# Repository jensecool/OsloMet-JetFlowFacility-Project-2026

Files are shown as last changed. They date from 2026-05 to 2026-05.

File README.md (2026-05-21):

# OsloMet Jet Flow Facility Project 2026

Technical information, firmware, 3D models, and documentation for the extended sub-sonic jet flow facility in the OsloMet Green Energy Lab. This repository continues the work of the 2025 group and adds quantitative airflow measurement to the facility.

## Project Background

This project is part of the European Project Semester (EPS) 2026 at Oslo Metropolitan University. Group 5 has extended an existing single-jet flow facility (originally built by Group 2 in 2025) with a differential pressure sensor and real-time velocity computation, turning a previously qualitative demonstration into a quantitative student experiment.

## Features

- **Fan Control:**
Adjustable fan speed via potentiometer and PWM output, with real-time RPM monitoring using a tachometer input.
- **Speaker Control:**
Potential for speaker volume adjustment via a second potentiometer.
- **Pressure and Velocity Measurement (new):**
Differential pressure across the stagnation chamber is read over I2C and converted to air velocity using Bernoulli's equation.
- **LCD Display:**
A Grove RGB LCD shows the fan speed, the live differential pressure (Pa), and the computed velocity (m/s). See the note below on the single versus dual screen configuration.
- **I2C Multiplexer:**
A TCA9548A multiplexer manages multiple I2C devices (the LCD(s) and the pressure sensor) on a single ESP32 I2C bus.
- **Switch Control:**
A momentary power switch toggles the fan system on and off using edge detection in firmware.
- **Multicore Task Management:**
Fan and switch handling tasks are pinned to separate ESP32 cores for parallel processing.

## Important Note: Single Screen vs Two Screens

The original design used two Grove RGB LCD screens: one for fan speed and one for pressure and velocity. During development the onboard 3.3V voltage regulator of the ESP32 was damaged, most likely during an earlier incident where the I2C hub was destroyed by a loose ground connection under power.

A healthy ESP32 regulator should output 3.3V. After the damage, the regulator only produces about 2.7V even with a healthy 5V input on VIN. This lower voltage is enough to power one LCD with readable contrast, but two LCD backlights together draw too much current, which pulls the voltage down further and makes the text on both screens too faint to read.

Because of this, the current working setup uses a single LCD that shows all values on one screen. When the ESP32 is replaced with a board that has a working 3.3V regulator, the two screen version can be used again.

Two firmware versions are provided:

- `esp-code/esp-code.ino` is the single screen version. All values (fan speed, velocity, and pressure) are shown on one LCD connected to hub channel 0. This is the version that works with the current damaged ESP32.
- `esp-code/esp_code-2screens/` contains the two screen version. Fan speed is shown on the LCD on hub channel 0, and pressure and velocity are shown on the LCD on hub channel 1. Use this version only with an ESP32 that has a healthy 3.3V regulator.

## Installation Instructions

### Hardware Requirements

- ESP32 NodeMCU-32S Development Board
- Fan motor with tachometer feedback (12V DC, 1.3A)
- 1x or 2x Grove RGB LCD V5.0 (I2C interface), depending on the firmware version used
- TCA9548A I2C multiplexer hub
- ELVH-M250D-HRRJ-I-N3A5 differential pressure sensor (±250 mbar, I2C address 0x38)
- Mean Well SD-15A-05 DC-DC converter (12V to 5V, 3A)
- Potentiometers (for fan speed and speaker volume)
- Switches (for power and speaker control)
- LEDs (for status indication)
- 50W audio amplifier with 5" 4Ω speaker
- Supporting resistors and wiring

### Software Requirements

- Arduino IDE (2.x or later)
- NodeMCU-32S board support (ESP32 boards package)

### Arduino Libraries

- `Wire.h`
- `Arduino.h`
- `rgb_lcd.h`

### Installation Steps

1. Clone this repository:
```bash
   git clone https://github.com/jensecool/OsloMet-JetFlowFacility-Project-2026.git
```

2. Open the firmware you need in the Arduino IDE:
   - `esp-code/esp-code.ino` for the single screen setup (current hardware)
   - `esp-code/esp_code-2screens/` for the two screen setup (requires a healthy ESP32)
3. Install the necessary libraries via the Library Manager.
4. Select the NodeMCU-32S board and the correct COM port.
5. Upload the code.

## Repository Structure

```
OsloMet-JetFlowFacility-Project-2026/
├── 3d models/         3D model files for printable enclosures and adapters
├── Circuit design/    Schematic diagrams of the electronics
├── esp-code/          ESP32 Arduino firmware (single and two screen versions)
├── Flowchart/         Flowcharts of the code logic and experiment process
└── Worksheet/         Student experiment worksheet
```

## ESP32 Pinout

| Function                | ESP32 Pin | Description                            |
|:------------------------|:----------|:---------------------------------------|
| Power Switch Input      | 5         | Toggles fan system ON/OFF              |
| Fan Speed Potentiometer | 34        | Analog read for fan speed setting      |
| Power LED Output        | 13        | Indicates fan system status            |
| Fan PWM Control         | 25        | PWM signal to control fan speed        |
| Fan Tachometer Input    | 14        | Reads pulses for RPM calculation       |
| I2C SDA                 | 21        | I2C data line to multiplexer hub       |
| I2C SCL                 | 22        | I2C clock line to multiplexer hub      |

## I2C Bus Layout

All I2C devices are connected through the TCA9548A multiplexer (address `0x70`) on the ESP32 bus:

| Hub Channel | Device                       | I2C Address     |
|:------------|:-----------------------------|:----------------|
| 0           | Main LCD (fan speed LCD)     | `0x30`, `0x3E`  |
| 1           | Pressure LCD (2 screen only) | `0x30`, `0x3E`  |
| 2           | Pressure sensor              | `0x38`          |
| 3 to 7      | Free                         | n/a             |

## Pressure Sensor Pinout

The ELVH-M250D-HRRJ-I-N3A5 sensor uses the HRRJ surface-mount J-lead package. Note that on this variant SCL is on pin 4, not pin 5 as the standard ELVH datasheet pin code table 1 suggests. The verified connections are:

| Sensor Pin | Function     | Wire Color |
|:-----------|:-------------|:-----------|
| 1          | GND          | Black      |
| 2          | Vs (3.3V)    | Red        |
| 3          | SDA          | White      |
| 4          | SCL          | Yellow     |
| 5 to 8     | Not connected| n/a        |

## Notes

- **Kickstart:** Fan starts at 100% PWM for 5 seconds on boot to overcome initial inertia.
- **I2C Multiplexer:** The project uses the TCA9548A I2C switch to manage the LCD(s) and the pressure sensor on the same I2C bus.
- **Power switch:** The APEM 5232 power switch is a momentary type. The firmware uses edge detection so that one press toggles the system on and the next press toggles it off.
- **Sensor zero offset:** The pressure sensor exhibits a small static offset (typically around 200 to 230 Pa) at zero airflow. This is normal manufacturing tolerance and should be subtracted from raw readings when computing absolute velocity values for analysis.
- **Velocity calculation:** Air velocity is computed using Bernoulli's equation `v = sqrt(2 * dP / rho)` with air density `rho = 1.225 kg/m^3`. Negative differential pressures are clamped to zero velocity in the firmware.

## Team

**Group 5, European Project Semester, OsloMet 2026:**
Jense Cool, Juan Trigueros, Alec Vroon, Siiri Vainopaa.

Supervisor: Ramis Örlü.

## Acknowledgements

This project builds upon the original jet-flow facility designed and constructed by **Group 2 (UFO – SSJFF) in 2025**: Finja Dittmann, Jelte Hoekstra, Robin Lind, Noud van der Meulen. Their report and original repository (`EPS-subsonic-jet-facility`) provided the hardware base, the smoke visualisation modules, and the acoustic forcing module that this work extends.

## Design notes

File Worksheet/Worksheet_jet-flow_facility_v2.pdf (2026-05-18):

European Project Semester, OsloMet 2026 - Group 5
Experiment: Quantitative fluid dynamics with the extended jet-flow facility

OSLO
MET
Jense Cool, Juan Trigueros, Alec Vroon, Siiri Vainopaa - Group 5 | Page 1

# Quantitative fluid dynamics with the extended jet-flow facility

## 1 Objective of the experiment

The aim of this experiment is twofold. First, students observe how a controlled stream of air behaves at different fan speeds and how an external sound source can disturb that stream. Second, and new in this version of the setup, students obtain a numerical measurement of the air velocity inside the facility by reading the differential pressure across the stagnation chamber and applying Bernoulli's equation. The facility therefore moves from a qualitative demonstration toward a small quantitative laboratory experiment.

By the end of the session the student should be able to relate a visible flow pattern to a measured pressure value, recognise the transition between laminar and turbulent regimes, and describe how acoustic forcing modifies a jet.

## 2 Theoretical fundamentals

### 2.1 Fluid dynamics

Fluid dynamics is the branch of physics that describes the motion of gases and liquids and the forces acting on them. It underpins applications as varied as aircraft design, weather prediction, blood flow modelling, and ventilation. In the laboratory it is usually approached through simplified geometries that isolate one phenomenon at a time, which is the role this facility plays.

### 2.2 The jet-flow facility

The setup used here is a single-jet wind facility. A fan draws ambient air through an intake, the airflow is conditioned by a diffuser followed by a honeycomb structure, and the resulting stream exits through a nozzle. The diffuser slows the flow so that the honeycomb can straighten it into parallel filaments, producing the laminar profile required for clean visualisation and measurement.

### 2.3 Smoke visualisation

Air on its own is invisible, so it has to be marked with a tracer to become observable. A small vaporiser produces a non-toxic glycol mist which is light enough to follow the local velocity field with very little lag. Once the mist is entrained in the airstream, the eye can clearly distinguish smooth laminar filaments from chaotic turbulent eddies.

### 2.4 Acoustic forcing

Sound consists of small periodic pressure fluctuations travelling through the air. When these fluctuations reach a jet, they perturb the shear layer at the edge of the stream and can trigger or suppress the natural instabilities that would otherwise grow further downstream. The result is a jet whose behaviour depends not only on the fan speed but also on the frequency and amplitude of the

Jense Cool, Juan Trigueros, Alec Vroon, Siiri Vainopaa - Group 5 | Page 2

imposed sound. This is referred to as acoustic forcing.

### 2.5 Pressure measurement and Bernoulli's principle

The extension added to the facility lets the user read the air velocity rather than estimate it visually. A differential pressure sensor sits between the stagnation chamber inside the facility and the ambient air outside. The difference between these two pressures, called the dynamic pressure, depends directly on the flow speed.

For an incompressible airflow at low speeds, Bernoulli's equation relates the dynamic pressure ∆P to the velocity v through:
v = √(2 · ∆P / ρ)

where ρ is the density of air, taken as 1.225 kg/m³
at standard room conditions. The microcontroller performs this calculation internally and displays both the raw pressure and the resulting velocity on the second LCD, so no manual computation is required during the session.

A few caveats are worth keeping in mind. Bernoulli's equation assumes a steady, frictionless, incompressible flow along a streamline. In a real jet these assumptions break down slightly, so the displayed velocity should be treated as a good estimate rather than an exact value. The sensor itself also has a small zero offset of roughly 200 Pa which appears as a non-zero reading even when the fan is off. Subtract this offset before drawing conclusions.

## 3 Work instructions

### 3.1 Preparing the facility

Verify before powering anything that the fan speed potentiometer (-SGA1) and the speaker volume control (-SGA2) are both turned fully counter-clockwise to the zero position. Plug the 12 V power supply (-TBA1) into a wall outlet and connect its barrel jack to the control panel inlet (-XDB1). Plug the amplifier (-TFA1) into a wall outlet using its dedicated mains cable (-XDB2). Press the power switch (-SJA1) on the control panel. The yellow LCD (-PHA1) should now show the current fan speed at 0 percent and the green LCD (-PHA2) should show a pressure reading near zero and a velocity near zero. Once both displays are active, the fan can be brought up by turning -SGA1 clockwise.

### 3.2 Reading the displays

Two LCD screens are mounted on the control panel. The yellow one shows the current fan speed as a percentage of full power, which corresponds to the position of the speed potentiometer. The green one shows two values: the differential pressure across the stagnation chamber in pascals, and the air velocity in metres per second derived from that pressure. The pressure value may oscillate by a few pascals as the sensor picks up small acoustic disturbances. This is normal and indicates that the sensor is working.

### 3.3 Smoke visualisation module

Slot the smoke machine (-HPB1) into the nozzle adapter (-NAD1) at the outlet end of the facility. Press the wireless smoke button (-SJB1) to release a puff of mist into the airflow. Vary the fan speed

Jense Cool, Juan Trigueros, Alec Vroon, Siiri Vainopaa - Group 5 | Page 3

(-SGA1) across its range and observe how the visible plume changes shape. At low speeds the smoke should travel in clean parallel layers. As the speed rises, the smoke breaks up into irregular swirling structures. Note your observations together with the corresponding pressure and velocity readings from the green LCD. Repeat the exercise with the smoke machine moved into the fan-side adapter (-NAD2) and compare the patterns at the same flow speeds.

### 3.4 Acoustic forcing module

For this part of the experiment the fan-side smoke adapter (-NAD2) should remain in place while the nozzle adapter (-NAD1) is removed. Attach the acoustic adapter (-XMB1) to the nozzle. Connect the audio cable (-XDB3) to the amplifier (-TFA1) on one end and to a phone or audio player on the other end. Toggle the speaker switch (-SJA2) to enable the speaker. Begin smoke production with (-SJB1) and play music while varying the volume with the speaker control (-SGA2). Try tracks of different genres, particularly those with strong low-frequency content, and document how the visible jet responds. Pay attention to any changes in the green LCD pressure reading during loud low-frequency passages.

### 3.5 Quantitative measurement procedure

This section is new compared to the previous version of the experiment and produces the numerical data needed for the analysis questions below.

Step 1. With the fan switched off, record the resting pressure value displayed on the green LCD. This is the sensor zero offset. Typical values fall in the range of 200 Pa to 230 Pa.
Step 2. Set the fan to 10 percent using -SGA1 and wait approximately ten seconds for the readings to stabilise. Note both the pressure and the velocity from the green LCD, together with the fan speed setting.
Step 3. Repeat at 25, 50, 75 and 100 percent fan speed. Five well spaced data points are sufficient.
Step 4. For each measurement, subtract the offset from Step 1 from the raw pressure reading. The corrected pressure is the value to use for any velocity calculation done by hand.
Step 5. Plot the corrected pressure on the vertical axis and the fan speed percentage on the horizontal axis. Then plot velocity against fan speed on a second graph. Compare the shapes of the two curves and connect them to the underlying physics in your analysis.

### 3.6 Analysis questions

Answer the following questions in your written submission. Combine visual observations from the smoke modules with numerical results from the pressure measurements where possible.

1) How does the visible behaviour of the airflow change as the fan speed increases?
2) At what approximate fan speed does the jet appear to transition from laminar to turbulent? Does this match the pressure or velocity reading at which it happens?
3) Which fluid dynamics principles explain the laminar to turbulent transition?
4) How does smoke visualisation help to interpret flow phenomena that would otherwise be invisible?

Jense Cool, Juan Trigueros, Alec Vroon, Siiri Vainopaa - Group 5 | Page 4
5) Using your recorded data, plot the measured velocity against fan speed percentage. Is the relationship linear, quadratic, or something else? Explain why this shape is expected.
6) Using your recorded data, plot the corrected pressure against fan speed percentage. How does this shape relate to the velocity curve?
7) Estimate the Reynolds number at maximum fan speed using a characteristic length equal to the nozzle diameter and a kinematic viscosity of 1.5 × 10⁻⁵ m²
/s. Does the value support your visual observation of laminar versus turbulent flow?
8) What effect does the acoustic forcing have on the visible airflow at different volumes and frequencies?
9) Through which physical mechanisms can sound waves modify the structure of a jet?
10) Discuss the main sources of measurement uncertainty in the pressure and velocity readings, and how the experiment could be improved.
11) Suggest a practical engineering application that could benefit from acoustic control of an airflow.

Jense Cool, Juan Trigueros, Alec Vroon, Siiri Vainopaa - Group 5 | Page 5

## 4 Material list

Component references follow the IEC 81346-2 standard. Items marked with an asterisk were added or modified in the current revision of the facility.

Reference | Name | Comment
-BPB1* | Pressure sensor | ELVH-M250D-HRRJ-I-N3A5; +/-250 mbar diff., I2C 0x38
-CAA1 | Capacitor | 1nF; 25V
-GQB1 | Jet-flow facility | Inherited from previous project group
-HMC1* | I2C multiplexer hub | TCA9548A based; 8 Grove ports; addr 0x70
-HPB1 | Smoke machine | Small vaporiser
-KEB1 | Microcontroller | ESP32 NodeMCU-32S
-MAA1 | Fan motor | 12VDC; 1.3A; 15.6W
-NAD1 | Smoke adapter nozzle | 3D-printed; two parts
-NAD2 | Smoke adapter fan | 3D-printed
-PFA1 | Power LED | 3V; 20mA; green
-PHA1 | Fan speed display | Grove RGB LCD V5.0; yellow backlight; I2C hub ch 0
-PHA2* | Pressure display | Grove RGB LCD V5.0; green backlight; I2C hub ch 1
-PJA1 | Speaker | 5 inch woofer; 4 Ohm
-RCA1 | Limiting resistor | 15 Ohm; series with -PFA1
-SGA1 | Fan speed control | 10 kOhm potentiometer
-SGA2 | Speaker volume level | Rotary knob on amplifier
-SJA1 | Power on/off | Momentary toggle switch
-SJA2 | Speaker on/off | Toggle switch
-SJB1 | Smoke trigger | Push button; wireless remote
-TAB1 | DC-DC converter | Mean Well SD-15A-05; 12VDC to 5VDC; 3A
-TBA1 | Power supply | 12VDC; 3A external brick
-TFA1 | Amplifier | 50W; 4 Ohm; t.amp PM40C
-UCA1 | Control panel | 3D-printed box; laser-cut top
-XDB1 | Control panel inlet | Barrel socket; 12VDC; 5A
-XDB2 | Cold device plug | 1.5m mains cable for amplifier
-XDB3 | Audio plug | 2.5m audio cable
-XMB1 | Acoustic adapter | 3D-printed with glued tubes

### 4.1 Note on the pressure sensor pinout

The ELVH-M250D-HRRJ-I-N3A5 uses the HRRJ surface-mount J-lead package. The Pin Code 1 table in the standard ELVH datasheet places SCL on pin 5, but on this particular variant SCL is on pin

Jense Cool, Juan Trigueros, Alec Vroon, Siiri Vainopaa - Group 5 | Page 6

4 and pin 5 is unused. The correct connections, verified empirically and confirmed by the supplier, are listed below.

Sensor pin | Function | Wire colour | Connects to
1 | GND | Black | Hub channel 2 GND
2 | Vs (supply, 3.3V) | Red | Hub channel 2 VCC
3 | SDA | White | Hub channel 2 SDA
4 | SCL | Yellow | Hub channel 2 SCL
5 to 8 | Not connected | n/a | Leave open

Jense Cool, Juan Trigueros, Alec Vroon, Siiri Vainopaa - Group 5 | Page 7

## 5 The experiment's set-up

The complete facility consists of the original jet-flow tube with its fan, smoke and acoustic modules, together with the extended control panel that now hosts two LCD screens and the pressure sensor measurement chain.

Key signal flow on the electronics side:

- The ESP32 microcontroller (-KEB1) runs the firmware and exposes a single I2C bus on its pins D21 (SDA) and D22 (SCL).
- This single I2C bus is fanned out to multiple downstream devices through the TCA9548A multiplexer hub (-HMC1).
- Channel 0 of the hub drives the fan speed LCD (-PHA1).
- Channel 1 of the hub drives the pressure and velocity LCD (-PHA2).
- Channel 2 of the hub connects to the pressure sensor (-BPB1) inside the stagnation chamber.
- Channels 3 to 7 are kept free for future expansion such as adding a temperature sensor or further user controls.

On the power side, the external 12 V supply (-TBA1) feeds both the fan and the on-board DC-DC converter (-TAB1), which steps the voltage down to 5 V for the ESP32 and the rest of the low-voltage electronics. The amplifier (-TFA1) has its own mains supply via a cold-device plug and drives the speaker (-PJA1) independently of the microcontroller, just as in the original setup.

A photograph of the assembled control panel and a wiring schematic are to be inserted here in the final document. The schematic should show the ESP32, the I2C multiplexer hub, both LCD displays, the pressure sensor, the fan motor, the LED, the toggle switches, the potentiometer and the DC-DC converter.

This worksheet is an updated revision of the original document produced by Group 2 (UFO – SSJFF): Finja Dittmann, Jelte Hoekstra, Robin Lind and Noud van der Meulen. The current revision was prepared by Group 5: Jense Cool, Juan Trigueros, Alec Vroon and Siiri Vainopaa, and extends the original facility with quantitative pressure and velocity measurement.

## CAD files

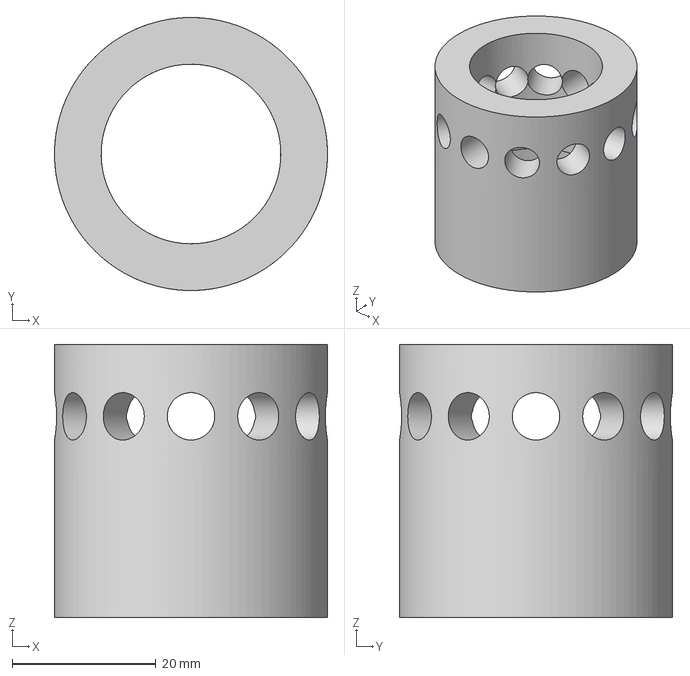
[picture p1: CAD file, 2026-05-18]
3d models/3dModels_2025/readyToPrint/Acoustic nozzle mount.3mf
38.0 x 38.0 x 38.0 mm

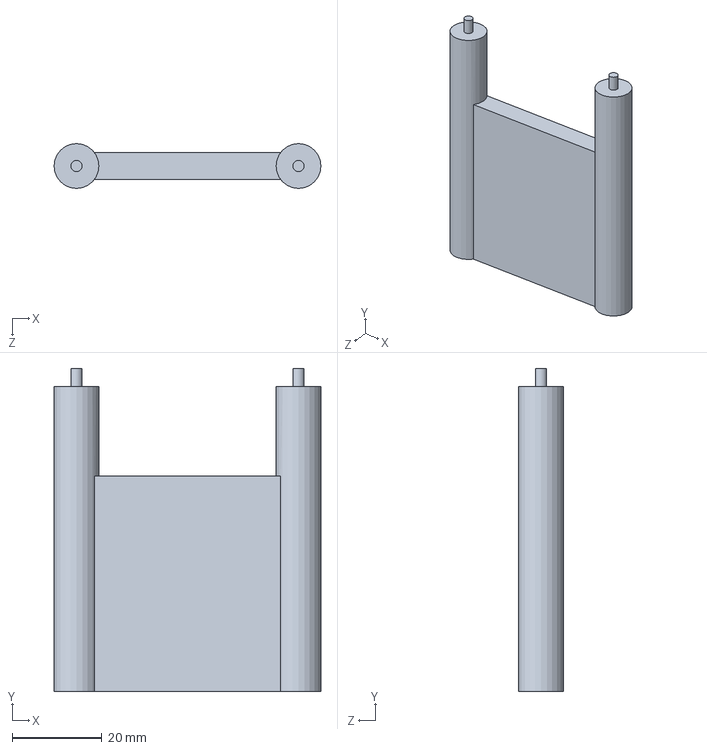
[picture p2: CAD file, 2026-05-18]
3d models/3dModels_2026/support windtunnel screen.SLDPRT
59.5 x 72.0 x 10.0 mm

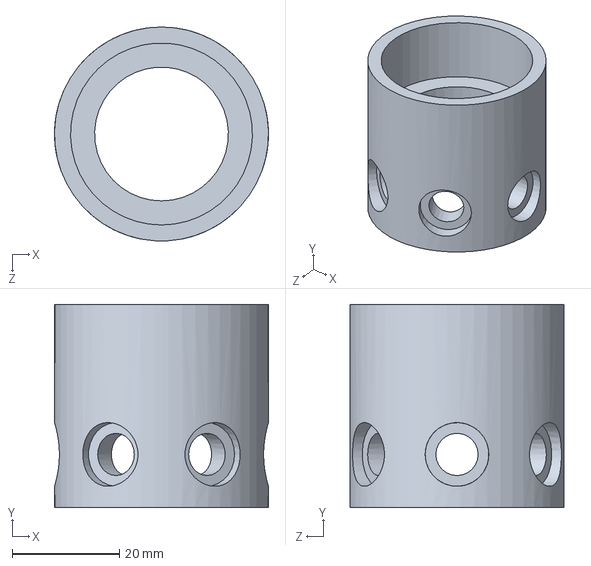
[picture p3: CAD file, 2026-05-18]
3d models/3dModels_2026/end nozle V2.SLDPRT
40.0 x 38.0 x 40.0 mm

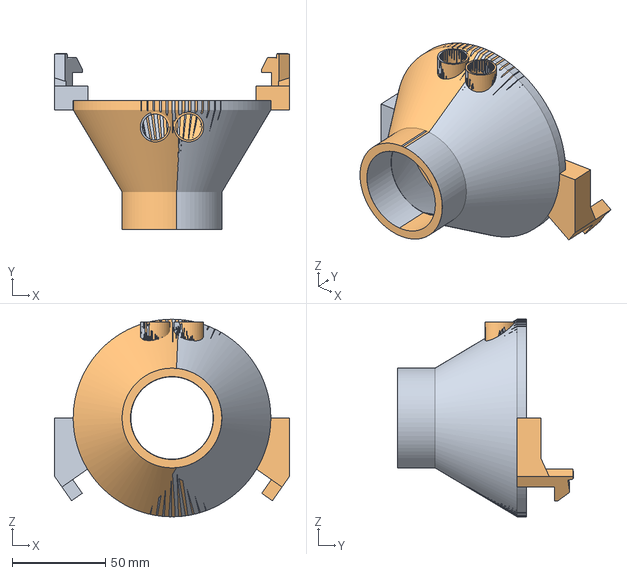
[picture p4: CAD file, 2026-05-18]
3d models/3dModels_2025/readyToPrint/Smoker around nozzle.3mf
126.1 x 94.2 x 106.0 mm

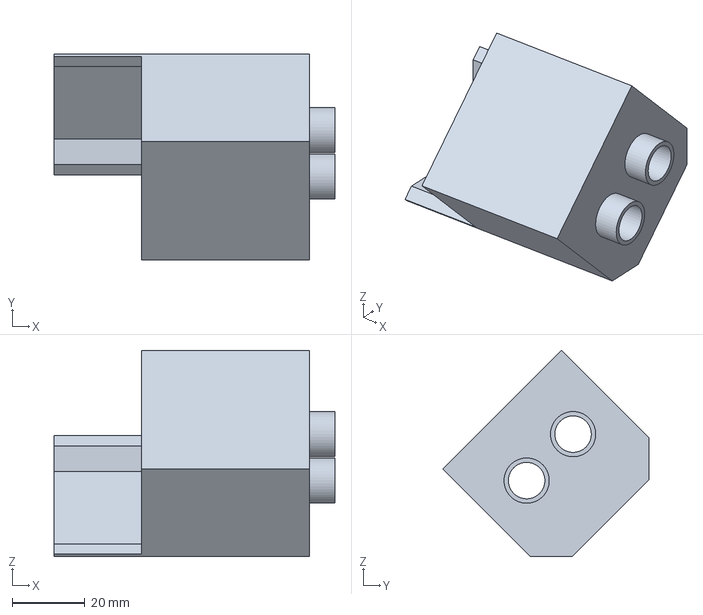
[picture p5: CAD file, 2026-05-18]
3d models/3dModels_2025/readyToPrint/Smoke holder design.3mf
77.0 x 56.6 x 56.6 mm

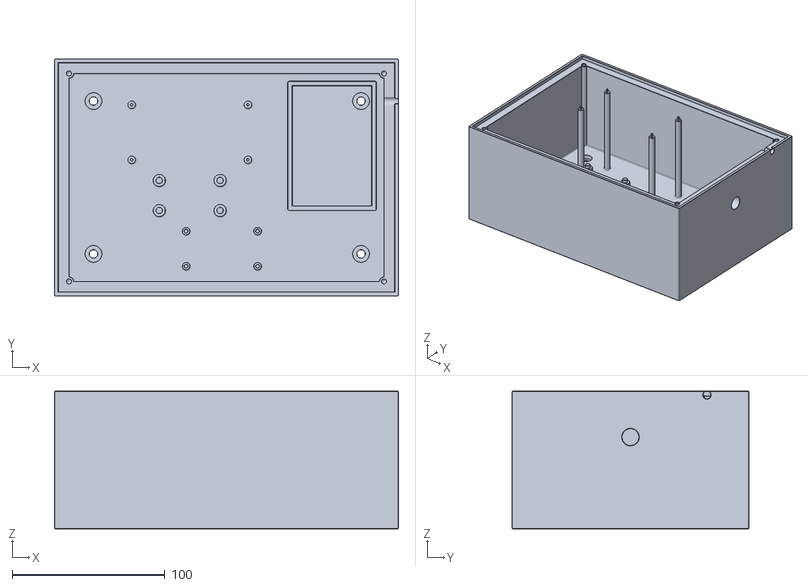
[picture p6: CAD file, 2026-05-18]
3d models/3dModels_2025/readyToPrint/ControlPanelBox version2.STL
225.0 x 155.0 x 90.0

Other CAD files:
3d models/3dModels_2025/readyToPrint/potentiometer caps.gcode.3mf
3d models/3dModels_2025/readyToPrint/Smoke fan intake.gcode.3mf
3d models/3dModels_2025/readyToPrint/Amp bracket.gcode.3mf
3d models/3dModels_2025/models/Acoustic nozzle mount.f3d
3d models/3dModels_2025/models/Smoker around Nozzle.f3d

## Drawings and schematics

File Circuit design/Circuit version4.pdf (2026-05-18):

12V

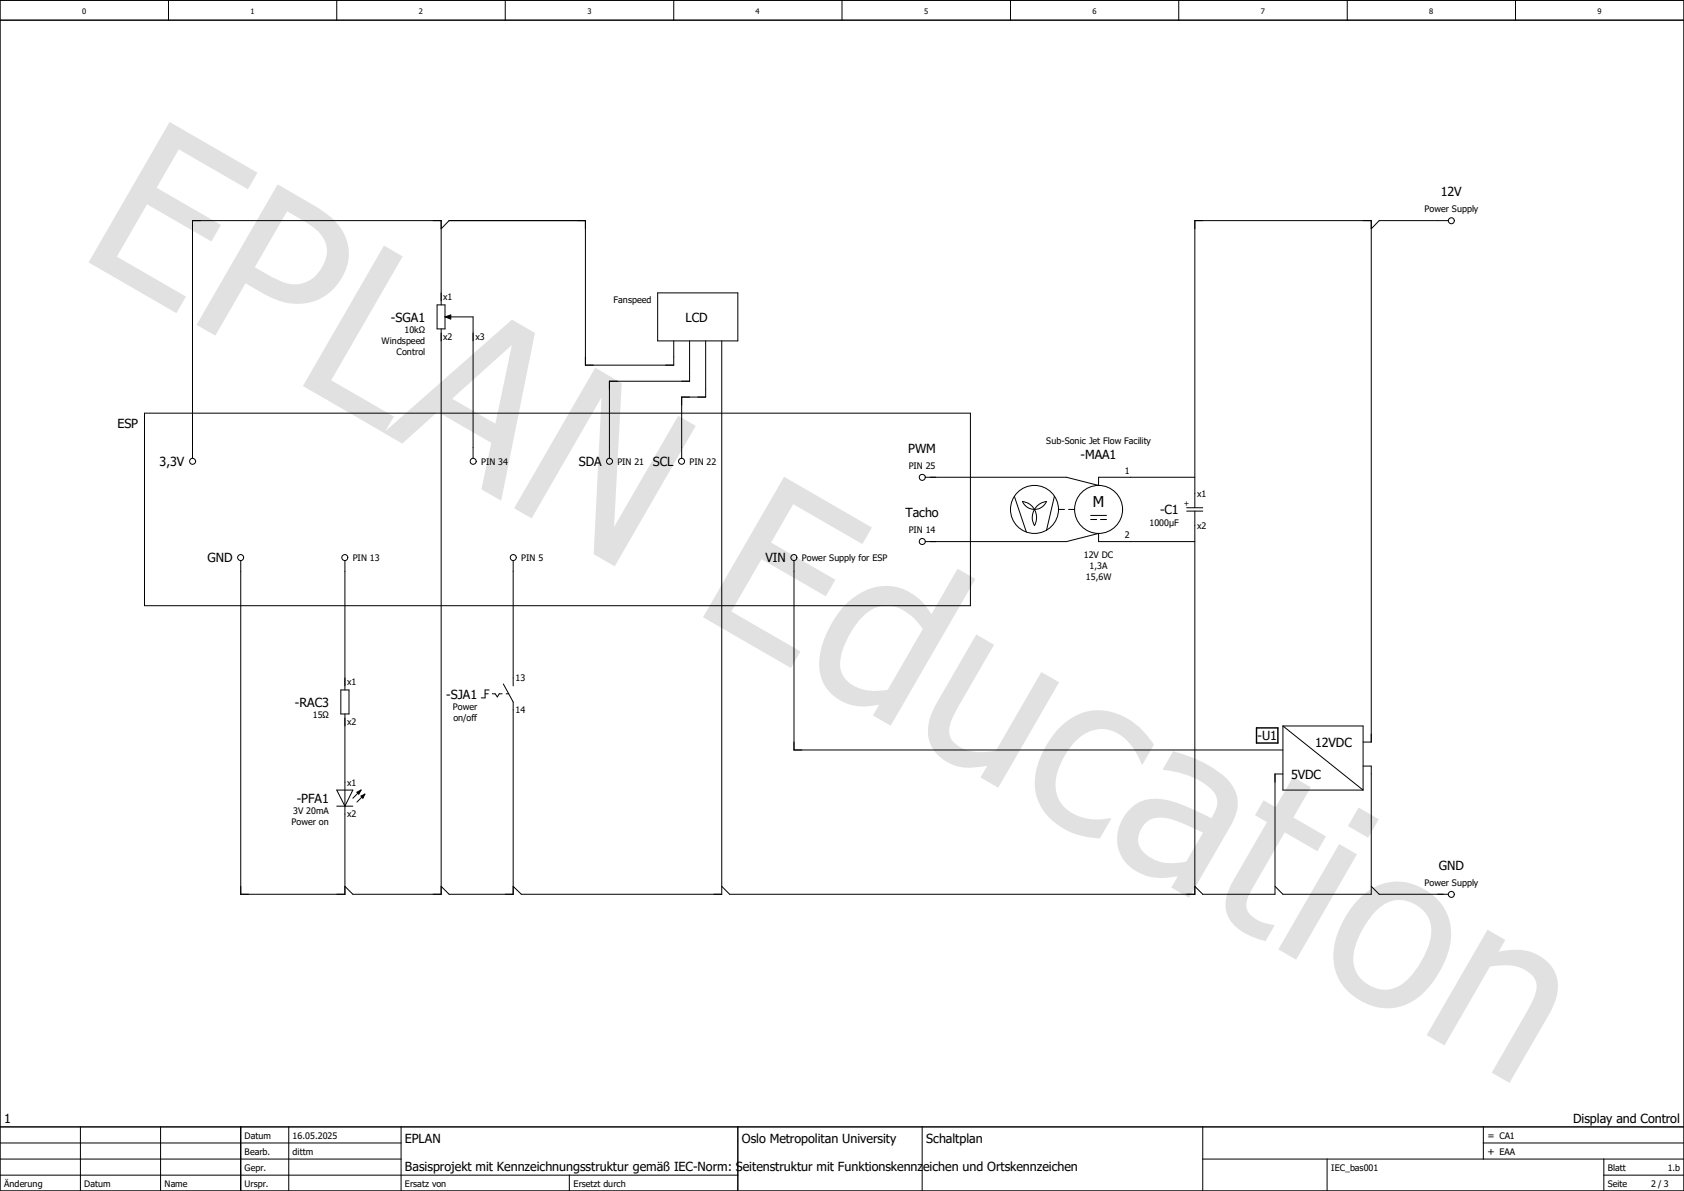
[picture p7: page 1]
12VDC; 5VDC; LCD; -SJA1 Power on/off; -PFA1 3V 20mA Power on; Power Supply; -SGA1 10kΩ Windspeed Control; GND; PIN 13; PIN 5; PIN 34; PIN 25; PWM; PIN 14; Tacho; -RAC3 15Ω; ESP; Fanspeed

Sub-Sonic Jet Flow Facility
-MAA1

SDA PIN 21 SCL PIN 22

VIN Power Supply for ESP

Display and Control

Datum | 16.05.2025 Oslo Metropolitan University | EPLAN Basisprojekt mit Kennzeichnungsstruktur gemäß IEC-Norm: Seitenstruktur mit Funktionskennzeichen und Ortskennzeichen | | Schaltplan | = CA1
Bearb. | dittm | | | | + EAA
Gepr. | | | | | IEC_bas001 | Blatt 1.b

Änderung | Datum | Name | Urspr. | | Ersatz von | Ersetzt durch | | | | Seite 2 / 3

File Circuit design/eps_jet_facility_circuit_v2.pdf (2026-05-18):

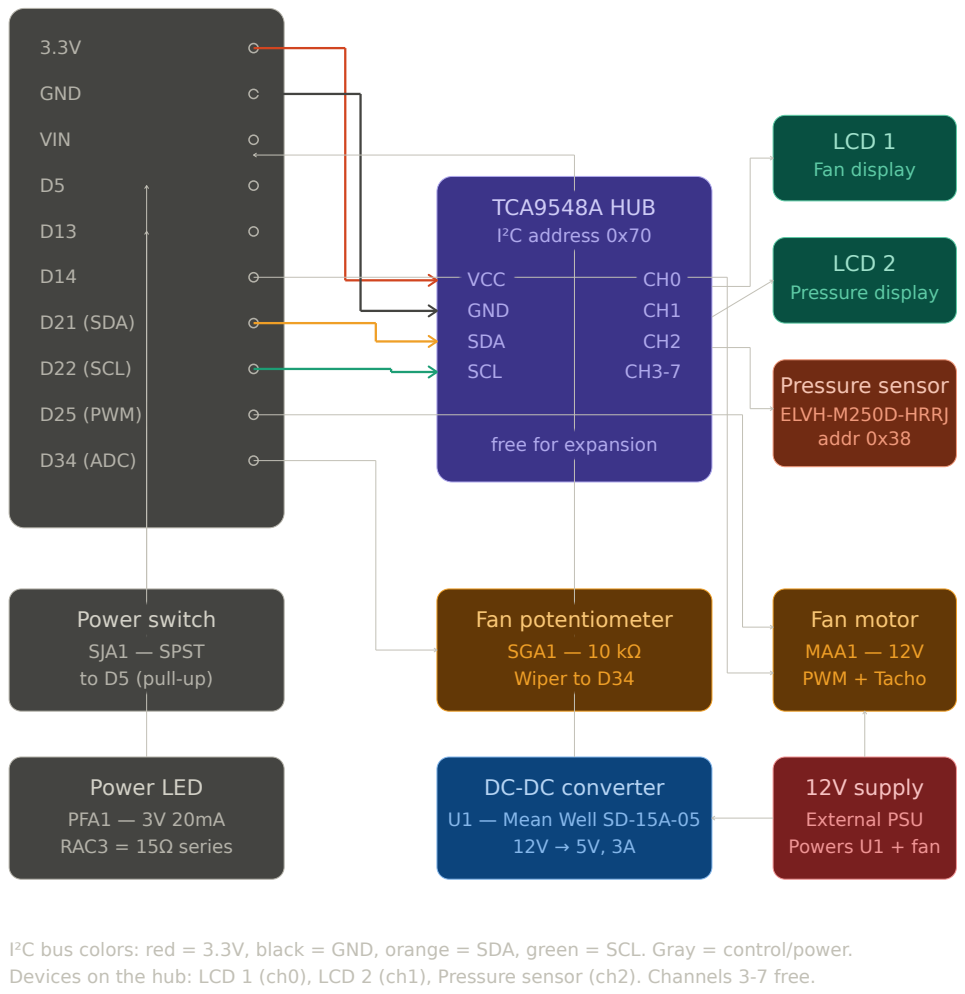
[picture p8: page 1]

I²C bus colors: red = 3.3V, black = GND, orange = SDA, green = SCL. Gray = control/power.
Devices on the hub: LCD 1 (ch0), LCD 2 (ch1), Pressure sensor (ch2). Channels 3-7 free.

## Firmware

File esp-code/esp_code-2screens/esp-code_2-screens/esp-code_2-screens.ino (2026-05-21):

#include <Wire.h>
#include <Arduino.h>
#include <math.h>
#include "rgb_lcd.h"

// === SWITCH PINS ===
#define POWER_SWITCH_PIN      5

// === POTENTIOMETER PINS ===
#define FAN_POT_PIN           34

// === LED PINS ===
#define POWER_LED_PIN         13

// === FAN PINS ===
#define FAN_PWM_PIN           25  // PWM control pin
#define FAN_TACHO_PIN         14  // RPM feedback pin

// === PWM CONFIG ===
#define PWM_FREQ              12500   // 12.5 kHz
#define PWM_CHANNEL           0
#define PWM_RESOLUTION        8       // 8-bit (0-255)

// === FAN SETTINGS ===
#define FAN_KICKSTART_SPEED   255     // Full speed
#define KICKSTART_DURATION    5000    // in milliseconds

// === I2C MULTIPLEXER ===
#define TCA_ADDR              0x70

// === PRESSURE SENSOR ===
#define SENSOR_ADDR           0x38      // ELVH-M250D-HRRJ-I-N3A5
#define SENSOR_OFFSET_COUNTS  8192.0f   // count at 0 Pa (differential, 10-90% TF)
#define SENSOR_FSS_COUNTS     6554.0f   // +/- full scale span in counts
#define SENSOR_FSS_PA         25000.0f  // +/-250 mbar = +/-25000 Pa

// Air density for Bernoulli.
#define AIR_DENSITY           1.225f

// === GLOBAL VARIABLES ===
volatile unsigned long pulse_count = 0;
unsigned long last_time = 0;
unsigned long rpm = 0;

bool power_on = false;
bool last_power_state = false;

int fan_speed = 178; // 70% default
int fan_speed_percentage = 0;

float pressure_pa = 0.0f;
float velocity_mps = 0.0f;
bool  sensor_present = false;

rgb_lcd lcd;
int fan_lcd_channel = 0;
int pressure_lcd_channel = 1;
int pressure_sensor_channel = 2;

// === FUNCTION DECLARATIONS ===
void tca_select(uint8_t channel);
void IRAM_ATTR count_pulse();
void calculate_fan_rpm();
void kickstart_fan();
void set_fan_speed();
void configure_fan_lcd(int channel);
void configure_pressure_lcd(int channel);
void reset_lcd(int channel);
int get_pot_value_percent(int pin);
int get_pot_value_8bit(int pin);
void handle_power_off();
void control_fan();
void control_pressure();
void control_panel_controller(void *pv_parameters);
void switches_controller(void *pv_parameters);
void scan_i2c_with_tca();
bool read_pressure_sensor(float *out_pa);
float pressure_to_velocity(float pa);


// === I2C Multiplexer Channel Select ===
void tca_select(uint8_t channel) {
    Wire.beginTransmission(TCA_ADDR);
    Wire.write(1 << channel);
    Wire.endTransmission();
    delay(10);
}

// === Tachometer Interrupt ===
void IRAM_ATTR count_pulse() {
    pulse_count++;
}

// === Calculate Fan RPM ===
void calculate_fan_rpm() {
    if (millis() - last_time >= 1000) {
        detachInterrupt(digitalPinToInterrupt(FAN_TACHO_PIN));
        rpm = (pulse_count * 30);  // 60s / 2 pulses = 30
        Serial.printf("Fan speed: %lu RPM\n", rpm);
        pulse_count = 0;
        last_time = millis();
        attachInterrupt(digitalPinToInterrupt(FAN_TACHO_PIN), count_pulse, FALLING);
    }
}

// === Kickstart Fan ===
void kickstart_fan() {
    Serial.println("Kickstarting fan...");
    ledcWrite(FAN_PWM_PIN, FAN_KICKSTART_SPEED);
    delay(KICKSTART_DURATION);
}

// === Set Fan Speed ===
void set_fan_speed() {
    ledcWrite(FAN_PWM_PIN, fan_speed);
}

// === Configure Fan LCD (channel 0) ===
void configure_fan_lcd(int channel) {
    tca_select(channel);
    delay(10);
    lcd.begin(16, 2);
    lcd.setRGB(255, 255, 0);  // Yellow backlight (fan LCD)
    lcd.setCursor(0, 0);
    lcd.print("Fan ready");
}

// === Configure Pressure LCD (channel 1) ===
void configure_pressure_lcd(int channel) {
    tca_select(channel);
    delay(10);
    lcd.begin(16, 2);
    lcd.setRGB(0, 255, 0);  // Green backlight (pressure LCD)
    lcd.setCursor(0, 0);
    lcd.print("Pressure + vel");
    lcd.setCursor(0, 1);
    lcd.print("Waiting sensor");
}

// === Clear LCD ===
void reset_lcd(int channel) {
    tca_select(channel);
    delay(10);
    lcd.setCursor(0, 0);
    lcd.print("                ");
    lcd.setCursor(0, 1);
    lcd.print("                ");
}

// === Read Potentiometer: % Output ===
int get_pot_value_percent(int pin) {
    uint16_t value = analogRead(pin);
    if (value <= 409) return 0; // Below 10% rounds to 0%
    return map(value, 409, 4095, 0, 100);
}

// === Read Potentiometer: 8-bit Output ===
int get_pot_value_8bit(int pin) {
    uint16_t value = analogRead(pin);
    if (value <= 409) return 0; // Below 10% rounds to 0%
    return map(value, 409, 4095, 26, 255);
}

// === Handle Power Off ===
void handle_power_off() {
    fan_speed = 0;
    pressure_pa = 0.0f;
    velocity_mps = 0.0f;
    reset_lcd(fan_lcd_channel);
    reset_lcd(pressure_lcd_channel);
    set_fan_speed();
}

// === Read the pressure sensor ===
bool read_pressure_sensor(float *out_pa) {
    tca_select(pressure_sensor_channel);

    uint8_t n = Wire.requestFrom(SENSOR_ADDR, (uint8_t)2);
    if (n != 2) {
        return false;
    }

    uint8_t b0 = Wire.read();
    uint8_t b1 = Wire.read();

    // top 2 bits of byte 0 are status; 00 means normal
    uint8_t status = (b0 >> 6) & 0x03;
    if (status != 0x00) {
        return false;
    }

    uint16_t raw = ((b0 & 0x3F) << 8) | b1;
    *out_pa = ((float)raw - SENSOR_OFFSET_COUNTS)
            / SENSOR_FSS_COUNTS
            * SENSOR_FSS_PA;
    return true;
}

// === Convert differential pressure to velocity via Bernoulli ===
float pressure_to_velocity(float pa) {
    if (pa <= 0.0f) return 0.0f;
    return sqrtf(2.0f * pa / AIR_DENSITY);
}

// === Fan Control (LCD on channel 0) ===
void control_fan() {
    fan_speed_percentage = get_pot_value_percent(FAN_POT_PIN);
    fan_speed = get_pot_value_8bit(FAN_POT_PIN);
    set_fan_speed();
    calculate_fan_rpm();

    char l0[17];
    snprintf(l0, sizeof(l0), "Fan speed: %d%%", fan_speed_percentage);

    tca_select(fan_lcd_channel);
    delay(10);
    lcd.setCursor(0, 0);
    lcd.print("                ");
    lcd.setCursor(0, 0);
    lcd.print(l0);
}

// === Pressure Control (LCD on channel 1) ===
void control_pressure() {
    float pa = 0.0f;
    sensor_present = read_pressure_sensor(&pa);

    tca_select(pressure_lcd_channel);
    delay(10);

    // Clear both lines first
    lcd.setCursor(0, 0);
    lcd.print("                ");
    lcd.setCursor(0, 1);
    lcd.print("                ");

    if (!sensor_present) {
        lcd.setCursor(0, 0);
        lcd.print("Sensor: missing");
        lcd.setCursor(0, 1);
        lcd.print("Check I2C ch 2");
        return;
    }

    pressure_pa = pa;
    velocity_mps = pressure_to_velocity(pa);

    char l0[17];
    char l1[17];
    snprintf(l0, sizeof(l0), "P: %6.1f Pa", pressure_pa);
    snprintf(l1, sizeof(l1), "v: %5.2f m/s", velocity_mps);

    lcd.setCursor(0, 0);
    lcd.print(l0);
    lcd.setCursor(0, 1);
    lcd.print(l1);

    Serial.printf("Pressure=%.1f Pa   Velocity=%.2f m/s\n",
                  pressure_pa, velocity_mps);
}

// === Control Panel Task (Core 0) ===
void control_panel_controller(void *pv_parameters) {
    configure_fan_lcd(fan_lcd_channel);
    configure_pressure_lcd(pressure_lcd_channel);

    while (1) {
        if (!power_on) {
            handle_power_off();
            last_power_state = false;
            delay(500);
            continue;
        }

        // If power JUST came back on, re-init both LCDs
        if (!last_power_state) {
            configure_fan_lcd(fan_lcd_channel);
            configure_pressure_lcd(pressure_lcd_channel);
            last_power_state = true;
            delay(100);
        }

        control_fan();
        control_pressure();
        delay(100);
    }
}

// === Switches Task (Core 1) ===
// Momentary switch with edge detection: one press toggles power_on.
void switches_controller(void *pv_parameters) {
    bool last_switch_reading = HIGH;  // INPUT_PULLUP: not pressed = HIGH

    while (1) {
        bool current_reading = digitalRead(POWER_SWITCH_PIN);

        if (last_switch_reading == HIGH && current_reading == LOW) {
            power_on = !power_on;
            digitalWrite(POWER_LED_PIN, power_on);
            Serial.printf("Fan is %s\n", power_on ? "ON" : "OFF");
            delay(50);  // short debounce
        }

        last_switch_reading = current_reading;
        delay(20);
    }
}

// === I2C Scanner for TCA ===
void scan_i2c_with_tca() {
    for (uint8_t ch = 0; ch < 8; ch++) {
        Serial.printf("Scanning channel %u\n", ch);
        tca_select(ch);
        delay(5);

        for (uint8_t addr = 1; addr < 127; addr++) {
            Wire.beginTransmission(addr);
            if (Wire.endTransmission() == 0) {
                Serial.printf("  Device found at 0x%02X\n", addr);
            }
        }
    }
}

// === Arduino Setup ===
void setup() {
    Serial.begin(115200);
    Wire.begin();

    pinMode(POWER_SWITCH_PIN, INPUT_PULLUP);
    pinMode(POWER_LED_PIN, OUTPUT);
    pinMode(FAN_TACHO_PIN, INPUT_PULLUP);

    ledcAttach(FAN_PWM_PIN, PWM_FREQ, PWM_RESOLUTION);
    attachInterrupt(digitalPinToInterrupt(FAN_TACHO_PIN), count_pulse, FALLING);

    xTaskCreatePinnedToCore(control_panel_controller, "controlPanelController", 10000, NULL, 1, NULL, 0);
    xTaskCreatePinnedToCore(switches_controller, "switchesController", 10000, NULL, 1, NULL, 1);

    kickstart_fan();
    last_time = millis();

    scan_i2c_with_tca();
}

// === Arduino Loop ===
void loop() {
    // Main logic is handled by tasks.
}

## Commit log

2026-05-18 Initial commit: firmware, worksheet, schematic, 3D models
    [Acoustic nozzle mount.3mf, Acoustic nozzle mount.f3d, Agarres.CATPart, Amp bracket.gcode.3mf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]
2026-05-21 Update: due to the problems with the elektronics. we made a solution with one screen. With another esp32 it should work with 2 screens.
2026-05-21 Update: Added the code when the esp32 is fixed/changed.
2026-05-21 Added: Flowchart
2026-05-24 Update: Calibration fix
